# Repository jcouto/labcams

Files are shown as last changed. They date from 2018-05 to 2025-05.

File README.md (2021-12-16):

                                             MMM
                                           MMMMMM
    MMM:               .MMMM             MMMM MMMMMMMM
    MMM:               .MMMM            MMMMM MMMMMMMM      
    MMM:               .MMMM             MMMM  MMMMMM        MM 
    MMM:  :MMMMMMMMM.  .MMMMOMMMMMM       MN     MMM      MMMMM 
    MMM:  :M     MMMM  .MMMMM?+MMMMM    MMMMMMMMMMMMMMM7MMMMMMM  
    MMM:         OMMM  .MMMM    MMMM    MMMMMMMMMMMMMMMMMMMMMMM 
    MMM:  .MMMMMMMMMM  .MMMM    ?MMM    MMMMMMMMMMMMMMMMMMMMMMM 
    MMM:  MMMM  .8MMM  .MMMM    ZMMM    MMMMMMMMMMMMMMMMMMMMMMM 
    MMM:  MMM=...8MMM  .MMMM    MMMM    MMMMMMMMMMMMMMM.MMMMMMM  
    MMM:  MMMMMMMMMMM  .MMMMMMMMMMM                        MMMM 
    MMM:   MMMMM 8MMM  .MMMM:MMMMZ                            M 

         MMMMMMN  =MMMMMMMM     MMMM.MMMM$ .+MMMM      MMMMMMM: 
       MMMMMMMMM  +MMMMMMMMM$   MMMMMMMMMMMMMMMMMM   MMMMMMMMM8 
      MMMM               MMMM   MMMM   MMMM    MMM+  MMM8       
      MMMZ          OMMMMMMMM   MMMM   NMMM    MMM?  MMMMMMM$   
      MMMI        MMMMM  MMMM   MMMM   NMMM    MMM?   ZMMMMMMMM 
      MMMM       7MMM    MMMM   MMMM   NMMM    MMM?        MMMM 
       MMMMD+7MM  MMMN   MMMM   MMMM   NMMM    MMM?  MM$:.7MMMM   
        MMMMMMMM  ZMMMMMOMMMM   MMMM   NMMM    MMM?  MMMMMMMM+  
                          https://bitbucket.org/jpcouto/labcams   

Multicamera control and acquisition.

This aims to facilitate video acquisition and automation of experimens, uses separate processes to record and store data. Interfaces with other computers via UDP or ZeroMQ for automating experiments. Uses hardware and FFMPEG to compress in real-time. 

## Instalation from pip (recommended but not the latest version):

``pip install labcams`` or add the ``--no-deps`` flag to install no dependencies.

Install camera [drivers](./camera_instructions.md):

## Usage:

Open a terminal and type ``labcams -h`` for help.

The first time you run ``labcams`` it will create a folder in the user home directory where the default preference file is stored.

### Command line options:

|       |  command     | description |
|-------|--------------|-------------|
| ``-w``| ``--wait``   | start with software trigger OFF |
| ``-t``| ``--triggered`` |  start with hardware trigger ON |
| ``-c X Y`` | ``--cam-select X Y``     |  start only some cameras ``-c 0 1`` |
| ``-d PATH`` | ``--make-config PATH``  |  create a configuration file |
| | ``--no-server`` | do not start the ZMQ nor the UDP server |

## Configuration files:

Configuration files ensure you always use the same parameters during your experiments.

The configuration files are simple ``json`` files. There are 2 parts to the files.

1. ``cams`` - **camera descriptions** - each camera has a section to store acquisition and recording parameters.

Available camera drivers:

 * `PCO` - install pco.sdk
 * `AVT` - install Vimba SDK and pymba
 * `QImaging` 
 * `pointgrey` - FLIR cameras - install Spinnaker
 * `openCV` - webcams and so on

For calcium or voltage imaging with the PCO (or another) camera use the arduino code in the ``duino`` folder and [instructions](./camera_instructions.md).

Each camera has its own parameters, there are some parameters that are common to all:

* `recorder` - the type of recorder `tiff` `ffmpeg` `opencv` `binary`
 * `haccel` - `nvidia` or `intel` for use with ffmpeg for compression.

**NOTE:** You need to get ffmpeg compiled with `NVENC` from [here](https://developer.nvidia.com/ffmpeg) - precompiled versions are avaliable - `conda install ffmpeg` works. Make sure to have python recognize it in the path (using for example `which ffmpeg` to confirm from git bash)/

**NOTE** To use `intel` acceleration you need to download the [mediaSDK](https://software.intel.com/content/www/us/en/develop/tools/media-sdk.html).

2. **general parameters** to control the remote communication ports and general gui or recording parameters.

 * `recorder_frames_per_file` number of frames per file
 * `recorder_path` the path of the recorder, how to handle substitutions - needs more info.

3. Aditional parameters:

 * 'CamStimTrigger' - controls the arduino camera trigger, see the duino examples folder.

### UDP and ZMQ:

``labcams`` can listen for UDP or ZMQ commands.

To configure use the command ``"server":"udp"`` in the end of the config file.

The port can be configured with ``"server_port":9999``

The UDP commands are:

 * Set the experiment name ``expname=EXPERIMENT_NAME``
 * Software trigger the cameras ``softtrigger=1`` (multiple cameras are not in sync)
 * Hardware trigger mode and save ``trigger=1``
 * Start/stop saving ``manualsave=1``
 * Add a message to the log ``log=MESSAGE``
 * Quit ``quit``

### Supported cameras -  [see instructions here](./camera_instructions.md):

 * PCO cameras (only windows)
 * PointGrey cameras (via PySpin)
 * Basler cameras (via pypylon)
 * Allied Vision Technologies (via pymba - updating to the latest)
 * QImaging cameras via the legacy driver (only windows)
 * Ximea cameras

### Features:

 * Separates viewer, camera control/acquisition and file writer in different processes.
 * Data from camera acquisition process placed on a cue.
 * Display options: background subtraction; histogram equalization; pupil tracking via the [ mptracker ](https://bitbucket.org/jpcouto/mptracker).	
 * Multiple buffers on Allied vision technologies cameras allows high speed data acquisition.
 * Online compression using ffmpeg (supports hardware acceleration)

## Instalation on Ubuntu 20.04

``sudo apt install python3-matplotlib ipython3 python3-opencv python3-pyqt5 python3-tqdm python3-pip python3-pyqtgraph python3-serial python3-zmq python3-natsort python3-pandas emacs git ssh ffmpeg``

``pip3 install labcams`` - this may end up in ``$HOME/.local/bin`` so add the following to the end of the ``.bashrc`` file: ``export PATH=$PATH:$HOME/.local/bin``

## Instalation - from git:

**Note:** On windows get the [ git bash terminal ](https://git-scm.com/downloads). I had issues running from cmd.exe when installed with conda.

1. Get [ anaconda ](https://conda.io/anaconda.html). Add conda to system PATH when asked. Open a terminal (use git bash if on windows) and type ``conda init bash``.
2. Clone the repository: ``git clone git@bitbucket.org:jpcouto/labcams.git``
3. Go into the cloned ``cd labcams`` folder.
4. Install the required packages, use e.g. ``pip install -r requirements.txt`` or conda install... 
5. Install ``labcams`` with ``python setup.py develop``
6. Follow the [camera specific instalation](./camera_instructions.md) and instructions for syncronization. Each camera must have a section in the ``~/labcams/default.json`` file that is created the first time you try to run the software with the command ``labcams`` from the terminal. Use a text editor to add the correct options. There are examples in the examples folder.
7. Install ffmpeg with anaconda: ``conda install -c conda-forge ffmpeg`` 

You can run ``labcams`` from the command terminal. 

**Please drop me a line for feedback and let the world know if you use this.**

Joao Couto - jpcouto@gmail.com

May 2017

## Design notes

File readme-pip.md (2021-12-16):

# labcams

A package for video acquisition and automation of experimens, uses separate processes to record and store data.

## Usage

Open a terminal and type ``labcams -h`` for help.

The first time you run ``labcams`` it will create a folder in the user home directory where the default preference file is stored.

## Configuration files:

Configuration files ensure you always use the same parameters during your experiments.

The configuration files are simple ``json`` files. There are 2 parts to the files.

A section were each camera is specified and a part with general parameters.

Available camera drivers:

* `PCO` - install pco.sdk
* `AVT` - install Vimba SDK and pymba
* `QImaging` 
* `pointgrey` - FLIR cameras - install Spinnaker
* `openCV` - webcams and so on

Each camera has its own parameters, there are some parameters that are common to all:

* `recorder` - the type of recorder `tiff` `ffmpeg` `opencv` `binary`
* `haccel` - `nvidia` or `intel` for use with ffmpeg for compression.
* 'CamStimTrigger' - controls the arduino camera trigger, see the duino examples folder.

## UDP and ZMQ:

``labcams`` can listen for UDP or ZMQ commands.

To configure use the command ``"server":"udp"`` in the end of the config file.

The port can be configured with ``"server_port":9999``

The UDP commands are:

* Set the experiment name - ``expname=EXPERIMENT_NAME``
* Software trigger the cameras (this is software, multiple cameras are not in sync) - ``softtrigger=1``
* Hardware trigger mode and save - ``trigger=1``
* Start/stop saving - ``manualsave=1``
* Add a message to the log - ``log=MESSAGE``
* Quit - ``quit``

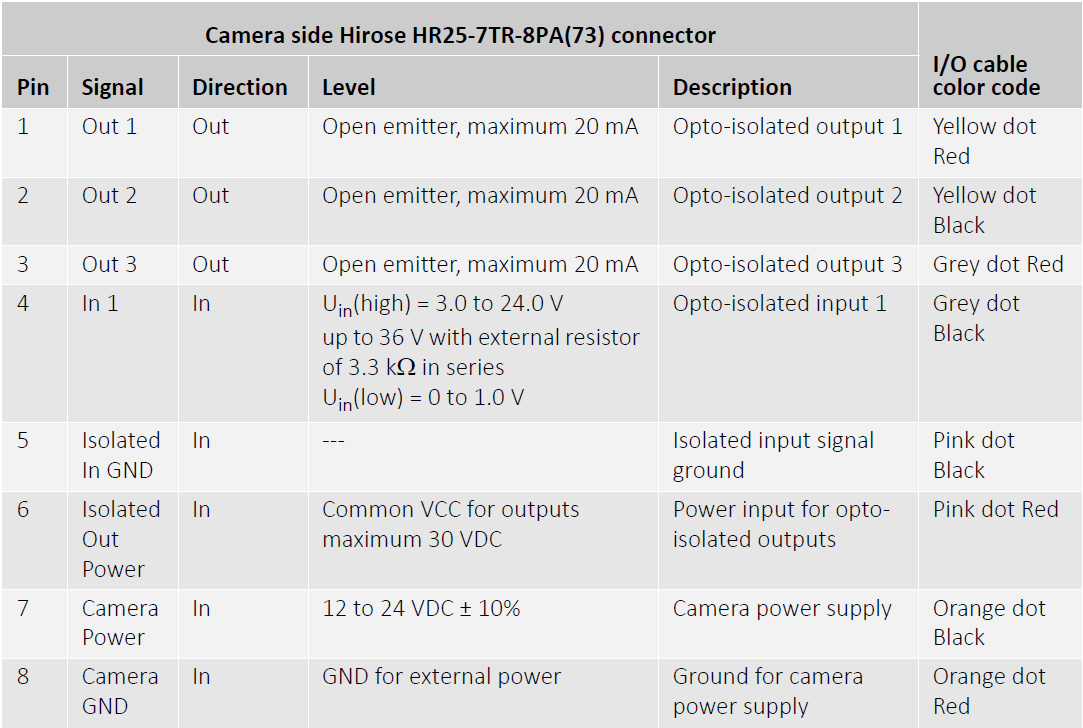
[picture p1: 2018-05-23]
images/mako_conn.png

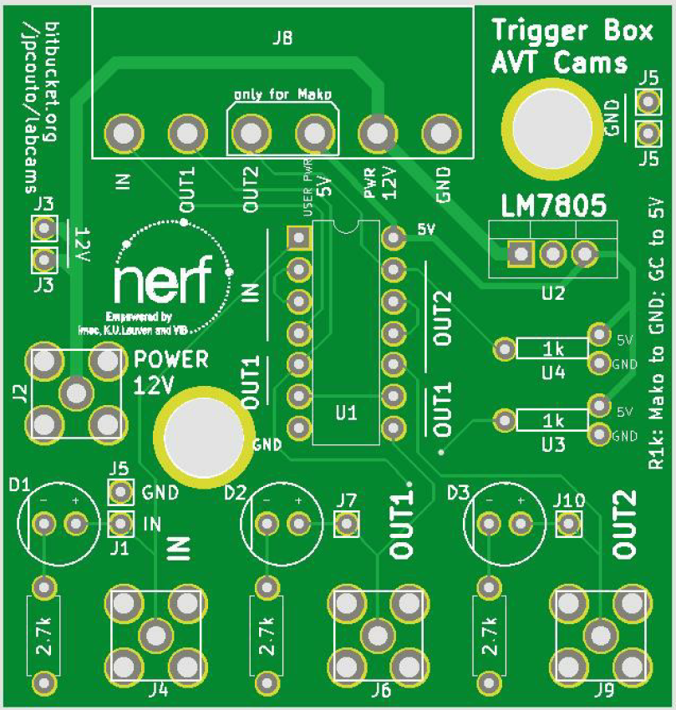
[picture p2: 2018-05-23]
images/trigger_box_avt.png

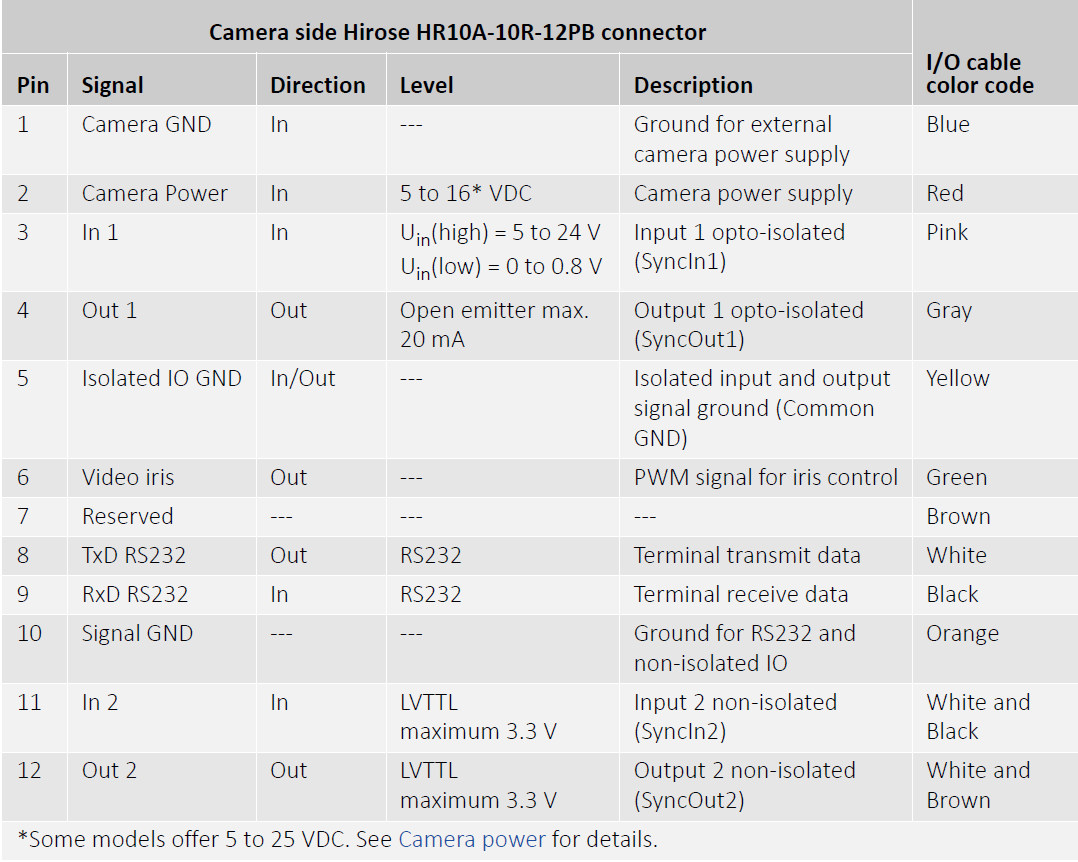
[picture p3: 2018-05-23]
images/gc_conn.png

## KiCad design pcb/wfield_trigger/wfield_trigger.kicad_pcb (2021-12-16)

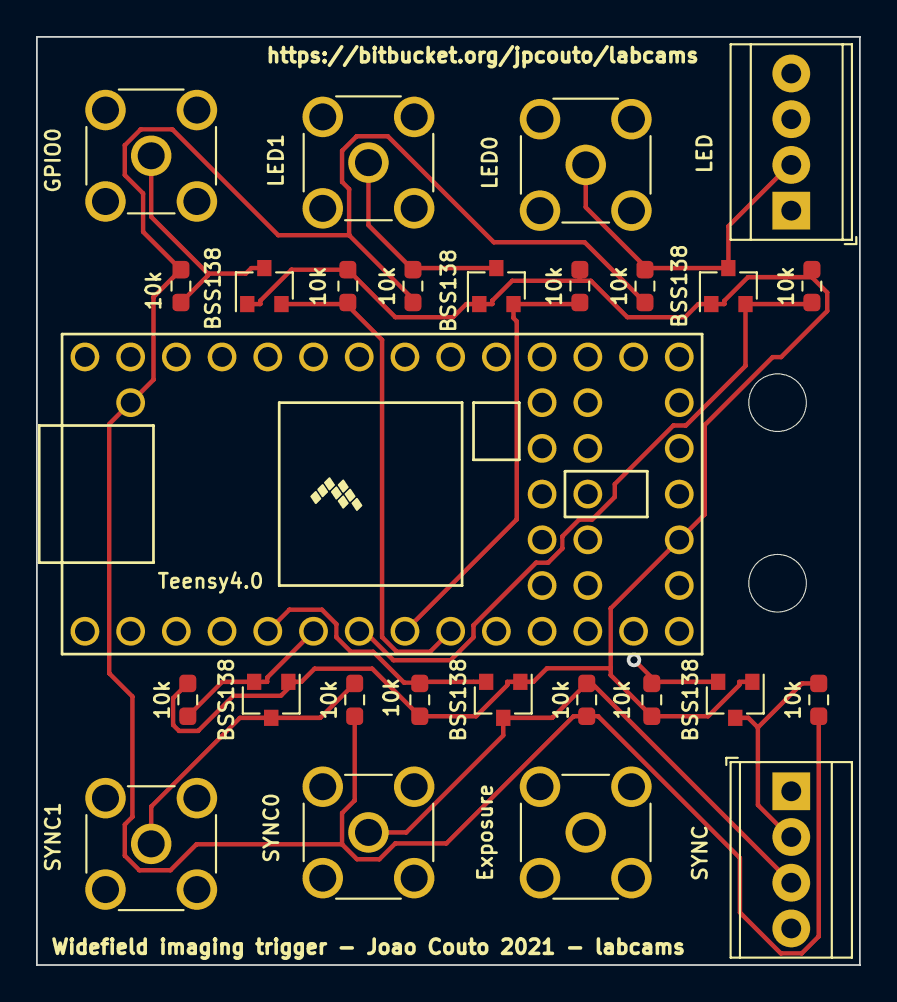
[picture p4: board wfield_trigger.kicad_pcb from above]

Board: 4 copper layers, 45.7 x 51.6 mm, 29 parts (0 on the bottom side), 15 nets.

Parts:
J1: SYNC; TerminalBlock_TE_282834-4_1x04_P2.54mm_Horizontal
J2: LED; TerminalBlock_TE_282834-4_1x04_P2.54mm_Horizontal
J3: LED1; SMA_Molex_73251-2200_Horizontal
J4: Exposure; SMA_Molex_73251-2200_Horizontal
J5: SYNC1; SMA_Molex_73251-2200_Horizontal
J6: SYNC0; SMA_Molex_73251-2200_Horizontal
J7: LED0; SMA_Molex_73251-2200_Horizontal
J8: GPIO0; SMA_Molex_73251-2200_Horizontal
Q1, Q2, Q3, Q4, Q5, Q6: BSS138; SOT-23
R1, R2, R3, R4, R5, R6, R7, R8, R9, R10, R11, R12: 10k; R_0603_1608Metric_Pad0.98x0.95mm_HandSolder
U1: Teensy4.0; Teensy40
mount1, mount2: MountingHole_3.2mm_M3

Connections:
+3V3: Q1.1, Q2.1, Q3.1, Q4.1, Q5.1, Q6.1, R2.1, R4.1, R6.1, R8.1, R10.1, R12.1, U1.16
+5V: R1.2, R3.2, R5.2, R7.2, R9.2, R11.2, U1.34
GND: J1.1, J2.1, J3.2, J4.2, J5.2, J6.2, J7.2, J8.2, U1.1, U1.17, U1.32
cam_trigger: Q1.2, R2.2, U1.4
cam_trigger_out: J1.2, J4.1, Q1.3, R1.1
gpio0: Q6.2, R12.2, U1.9
gpio0_out: J2.4, J8.1, Q6.3, R11.1
led0: Q4.2, R8.2, U1.7
led0_out: J2.2, J7.1, Q4.3, R7.1
led1: Q5.2, R10.2, U1.8
led1_out: J2.3, J3.1, Q5.3, R9.1
sync0: Q2.2, R4.2, U1.5
sync0_out: J1.3, J6.1, Q2.3, R3.1
sync1: Q3.2, R6.2, U1.6
sync1_out: J1.4, J5.1, Q3.3, R5.1

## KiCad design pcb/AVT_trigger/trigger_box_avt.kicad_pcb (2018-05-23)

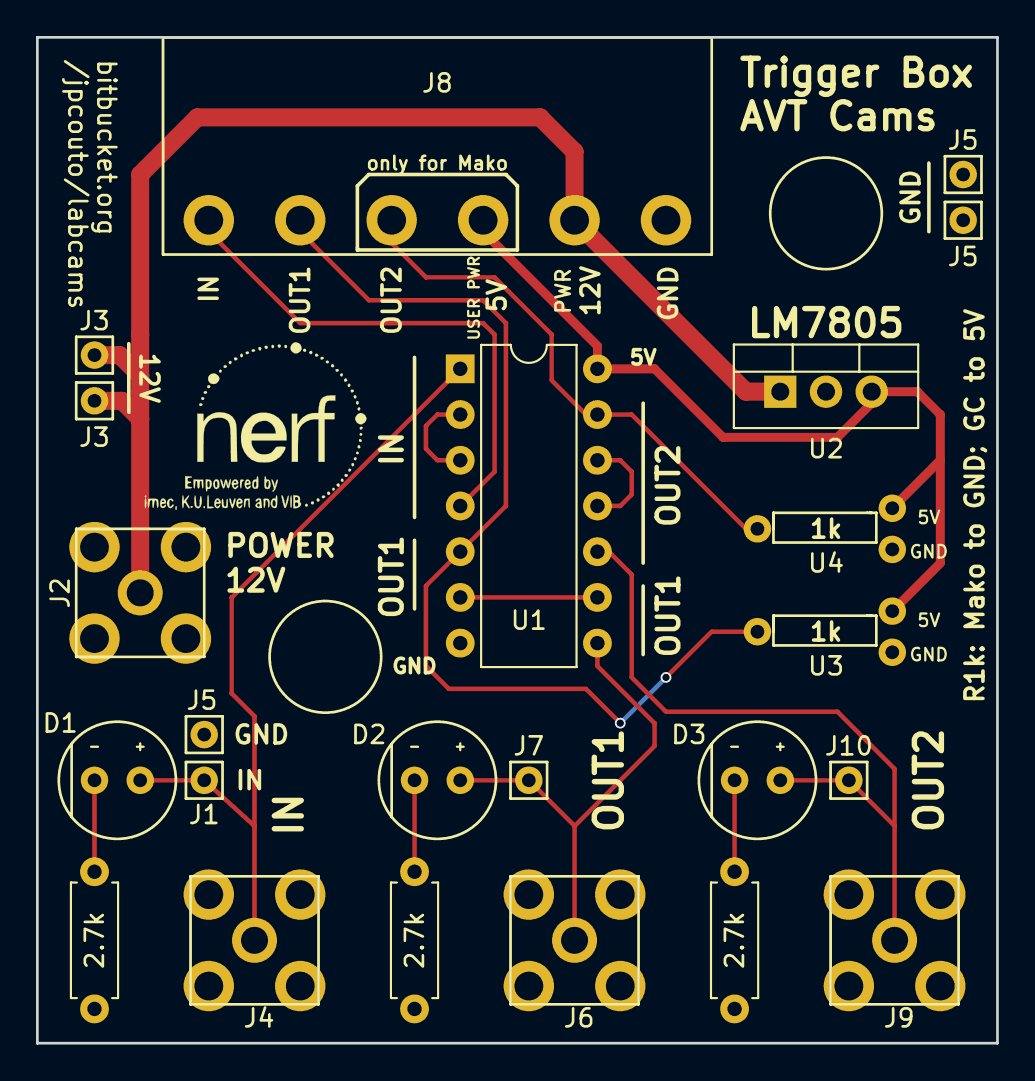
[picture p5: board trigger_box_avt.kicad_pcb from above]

Board: 2 copper layers, 53.3 x 55.9 mm, 23 parts (0 on the bottom side), 15 nets.

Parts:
2.7k, 2.7k#2, 2.7k#3: R; R_Axial_DIN0207_L6.3mm_D2.5mm_P7.62mm_Horizontal
D1, D2, D3: LED; LED_THT_standard
J1, J3, J3#2, J5, J5#2, J5#3, J7, J10: Conn_01x01; conn_01x01
J2, J4, J6, J9: Conn_Coaxial; SMA_female
J8: Conn_01x06; Conn_1x6
U1: 74hct14; DIP-14_W7.62mm
U2: LM7805_TO220; TO-220-3_Vertical
U3, U4: Resistor_choice; Resistor_THT_choice

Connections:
+5V: J8.4, U1.14, U2.3, U3.2, U4.2
+12V: J2.1, J3.1, J3#2.1, J8.5, U2.1
GND: 2.7k.2, 2.7k#2.2, 2.7k#3.2, J1.1, J2.2, J4.2, J5.1, J5#2.1, J6.2, J8.6, J9.2, U1.7, U2.2, U3.3, U4.3
unnamed: 2.7k.1, D1.1
unnamed: 2.7k#2.1, D2.1
unnamed: 2.7k#3.1, D3.1
unnamed: D1.2, J4.1, J5#3.1, U1.1
unnamed: D2.2, J6.1, J7.1, U1.8
unnamed: D3.2, J9.1, J10.1, U1.10
unnamed: J8.1, U1.4
unnamed: J8.2, U1.5, U3.1
unnamed: J8.3, U1.13, U4.1
unnamed: U1.2, U1.3
unnamed: U1.6, U1.9
unnamed: U1.11, U1.12

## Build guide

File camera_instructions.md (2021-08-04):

## Camera specific instructions

# PCO Edge

### Installing drivers and connecting the camera

This camera only works in windows.

Install the PCO.sdk software; make sure to install the correct adapter for your camera (e.g. CameraLink if you have a frame grabber). Install to one of the locations below.

labcams searches for the drivers in:

 * C:\Program Files (x86)\pco\pco.sdk\bin64\SC2_Cam.dll
 * C:\Program Files (x86)\Digital Camera Toolbox\pco.sdk\bin64\SC2_Cam.dll or
 * C:\Program Files (x86)\PCO Digital Camera Toolbox\pco.sdk\bin64\SC2_Cam.dll

**CRITICAL:** For now the PCO camlink camera needs to be initialized before it can be used. You need to open the camera with Camware before opening with ``labcams``. This needs to be done everytime you restart the computer or change the size of the sensor. Change camera properties with CamWare, these will stay

# Connections for widefield imaging using a teensy for sync and alternate illumination

For fast one photon imaging with the PCO (or another) camera you want to use the camera in **rolling shutter mode**. To do this light needs to be ON only during the exposure time common to all lines. These options need to be set in the camera software.

**NOTE:** If CamWare does not have the settings menu available; go to: File -> Options -> Show Camera Control and set it to "Yes".

You can use a teensy to record sync pulses from behavior or stimulus (e.g. using a photodiode on visual display). There are a couple of examples in the duino folder.

Connect the teensy as follows:
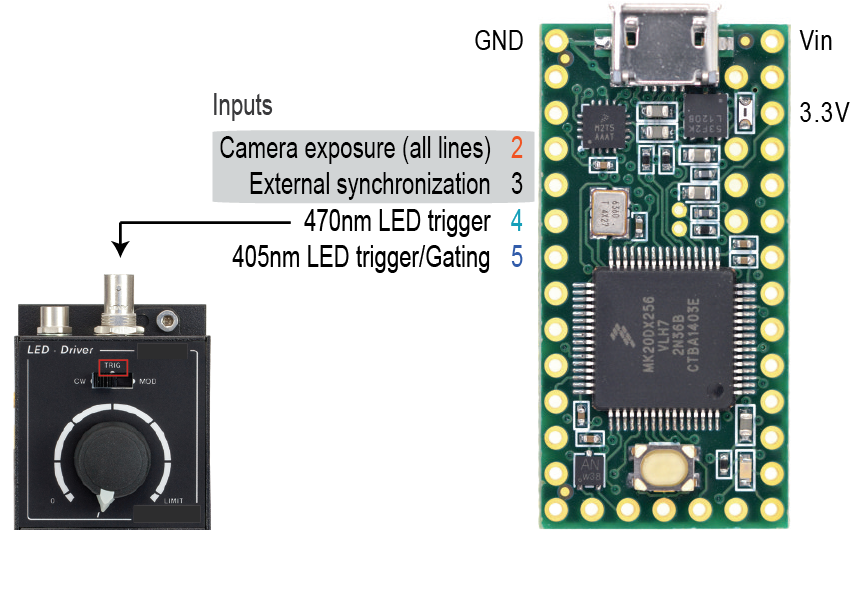
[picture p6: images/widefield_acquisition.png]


The teensy code uses interrupts so that we keep count of even and odd frames.

# Basler cameras

Install the Basler camera drivers "pylon" and the python API.
The python API can be installed with the command ``pip install pypylon`` 

# FLIR cameras

### Installing drivers and connecting the camera

Download SpinView **both the instalation .exe and the python files**. 

**WARNING** Do not do ``pip install pyspin`` the pyspin package in the PyPi project is not the same as the SpinView Python drivers.

* Install the exe
* To install for python you need to download the correct  version for your python instalation (from the FLIR SpinView website).
* Extract the zip and run ``pip install spinnaker_python-2.0.0.147-cp38-cp38-win_amd64.whl`` from the extracted folder (assuming you are using python 3.8).

### Connections for syncronization

To record in sync with behavior you need to connect a **sync TTL** (this from behavior or stimulation hardware) to the pins of the camera. 

On the Chamaeleon 3 USB you can use the Purple wire (GPIO 2). The GPIO states are recorded to the log file and you can use those to sync. 

Make sure the sync pulse is longer than the duration of an individual frame otherwise the camera might miss it.  

# Allied Vision Technologies cameras (AVT):

### Installing drivers and connecting cameras:

* Vimba drivers
* Pymba
* Jumbo packets
* Cable connections and diagram 
     general (camera, computer,ethernet,triggering box)
Connect the Ethernet cable to your computer.
Typically, Vimba Viewer recognizes the camera, but you can not record.
If this is the case then you have to change your IP address. 
On Windows: Control Panel -> Network & Internet -> Network connections -> right-click Ethernet -> Properties -> Networking: Select IPv4 -> Properties -> Use the following IP address. Then change it to a value close to the one of the camera (accessible in the Vimba Viewer in the �information� tab on the right). In my case I used 168.254.100.0 for the IP address and 255.255.0.0 for the subnet mask.

##### Connections for the GC camera

We are only using the first 5 pins of the camera.

Camera Signal|Wire Color|Trigger box pin
------------ | -------- | --------------
Camera GND|Blue|GND
Camera Power|Red|PWR 12V
In 1| Pink|IN
Out 1|Gray|OUT1
Isolated IO GND|Yellow|GND

GC Hirose HR10A-10R-12PB connector [Complete table](images/gc_conn.png)
 
##### Connections for the Mako

We are using 7 pins of the camera (all except Out3).

Camera Signal|Wire Color|Trigger box pin
------------ | -------- | --------
Out 1|Yellow dot Red|OUT1
Out 2|Yellow dot Black|OUT2
In 1|Grey dot Black|IN
Isolated In GND|Pink dot Black|GND
Isolated Out Power|Pink dot Red|USER PWR 5V
Camera power|Orange dot Black|PWR 12V
Camera GND|Orange dot Red|GND

Mako Hirose HR25-7TR-8PA(73) connector [Complete table](images/mako_conn.png)

### Triggering printed circuit board
The triggering printed circuit board has been tested with AVT cameras. It can be used to
   - power cameras;
   - access the camera output
   - trigger cameras with TTL signals.

It uses a schmitt trigger for normalizing the outputs

#### Circuit diagram

Power is on the left, camera interface on top and Arduino interface on bottom.
Only 2 outputs are used: the GC can only use 1, and while the Mako can use up to 3, there is no likely scenario where 3 outputs are needed.

The two main components of the board are a Hex Inverter with Schmitt trigger (74HCT14) and a voltage regulator (LM7805).


The schematics and PCB were done in KiCad ([Design files](pcb/)) by Adrian Philippon in the Bonin Lab at NERF.

* There is an indicator LED for each trigger connection.
* The 1k resistors (U3 and U4) are the pull up/down resistors for the camera outputs, and can be connected either to 5V (for the AVT GC) or GND (for the AVT Mako).
* Some pins are repeated (e.g. 12V, GND) to allow juxtaposition of several trigger boxes. This allows several boards to share the same power supply and trigger source.
* The two holes are M6.

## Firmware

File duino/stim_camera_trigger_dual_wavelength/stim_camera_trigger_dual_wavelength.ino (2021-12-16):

const byte PIN_CAM_EXPOSURE = 2;
const byte PIN_SYNC0 = 3;
const byte PIN_SYNC1 = 4;
const byte PIN_LED0_TRIGGER = 5;
const byte PIN_LED1_TRIGGER = 6;
const byte PIN_GPIO = 7;
#define GPIO_MIMIC_EXPOSURE
volatile long current_time = 0;
volatile long start_time = 0;
volatile long last_pulse_count = 0;
volatile long last_rise = -1;
volatile byte last_led = 0;

//sync counts
volatile long last_sync_rise = -1;
volatile long sync_count = 0;
volatile long sync_frame_count = 0;

volatile long pulse_count = 0; // number of pulses to trigger
volatile byte mode = 3;       // mode 0 : trigger the camera only
                              // mode 1 : LED0
                              // mode 2 : LED1
                              // mode 3 : LEDs alternate
volatile byte armed = 0;      // whether the triggers are armed  

// Serial communication
#define STX '@'
#define ETX '\n'
#define SEP "_"
#define CAP "NCHANNELS_2_MODES_470nm:405nm:both" // capabilities for interfacing with labcams
#define QUERY_NCHANNELS 'C'
#define QUERY_CAP 'Q'
#define START_LEDS 'N'
#define STOP_LEDS 'S'
#define FRAME 'F' // signal the frame time
#define SYNC 'T' // signal the sync time

//#define SET_PARAMETERS 'P' // placeholder
#define SET_MODE 'M' // set the width and the delay

// Serial communication "receive"
# define MSGSIZE 64
char msg[MSGSIZE];
int cnt = 0;

// interrupt to handle flipping the LEDS
void camera_triggered() {
  if (digitalReadFast(PIN_CAM_EXPOSURE) == LOW) {
        digitalWriteFast(PIN_LED0_TRIGGER, LOW);
      digitalWriteFast(PIN_LED1_TRIGGER, LOW);  
      #ifdef GPIO_MIMIC_EXPOSURE
        digitalWriteFast(PIN_GPIO, LOW);
       #endif
  } else {
    
  if (armed) {
    pulse_count++;
    // set the time of the next pulse
    byte pin;
    switch (mode) {
      case 1:
          pin = PIN_LED0_TRIGGER;
          break;
      case 2:
          pin = PIN_LED1_TRIGGER;
          break;
      case 3:
      {
        int tmp = pulse_count % 2;
        if (tmp == 0)
          pin = PIN_LED1_TRIGGER;
        else
          pin = PIN_LED0_TRIGGER;
      }
        break;
      default:
          pin = PIN_LED0_TRIGGER;
    }
    digitalWriteFast(pin, HIGH);
    #ifdef GPIO_MIMIC_EXPOSURE
      digitalWriteFast(PIN_GPIO, HIGH);
    #endif
    last_rise = millis() - start_time;
    last_led = pin;
    last_pulse_count = pulse_count;    
  }
}
}

void sync_received() {
  if (digitalReadFast(PIN_SYNC0) == HIGH)
    sync_count++;
  sync_frame_count = pulse_count;
  last_sync_rise = millis() - start_time;
  }


void setup() {
  pinMode(PIN_LED0_TRIGGER, OUTPUT);
  pinMode(PIN_LED1_TRIGGER, OUTPUT);
  pinMode(PIN_GPIO, OUTPUT);
  pinMode(PIN_SYNC0, INPUT);
  pinMode(PIN_SYNC1, INPUT);
  pinMode(PIN_CAM_EXPOSURE, INPUT);

  digitalWriteFast(PIN_LED0_TRIGGER, LOW);
  digitalWriteFast(PIN_LED1_TRIGGER, LOW);

  Serial.begin(2000000);
  attachInterrupt(digitalPinToInterrupt(PIN_CAM_EXPOSURE), camera_triggered, CHANGE);
  attachInterrupt(digitalPinToInterrupt(PIN_SYNC0), sync_received, CHANGE);
  start_time = millis(); // use micros if more precision needed
}

void loop() {
  current_time = millis() - start_time;
  if ((last_rise > 0) & (abs(current_time - last_rise)> 10)) { // this is limited to 10ms
    Serial.print(STX);
    Serial.print(FRAME);
    Serial.print(SEP);
    Serial.print(last_led);
    Serial.print(SEP);
    Serial.print(last_pulse_count);
    Serial.print(SEP);
    Serial.print(last_rise);
    Serial.print(ETX);
    last_rise = -1;
  }
  if (last_sync_rise > 0){ // this is limited to 10ms
    Serial.print(STX);
    Serial.print(SYNC);
    Serial.print(SEP);
    Serial.print(sync_frame_count);
    Serial.print(SEP);
    Serial.print(sync_count);
    Serial.print(SEP);
    Serial.print(last_sync_rise);
    Serial.print(ETX);
    last_sync_rise = -1;
}
}
void serialEvent()
{
  while (Serial.available()) {
    char ch = Serial.read();
    char* token;
    if (ch == STX || cnt > 0) {
      msg[cnt] = ch;
      cnt++;
      if (ch == ETX) {
        cnt = 0;
        String reply = String(STX);
        switch (msg[1]) {
          case START_LEDS:
            // @N
            last_sync_rise = -1;
            last_rise = -1;
            start_time = millis();
            pulse_count = 0;
            sync_frame_count = 0;
            sync_count = 0;
	    last_pulse_count = 0;
            armed = 1;
            
            reply += START_LEDS;
            Serial.print(reply);
            Serial.print(SEP);
            Serial.print(current_time);
            Serial.print(ETX);
            break;
        case STOP_LEDS:
            // @S
            armed = 0;
            reply += STOP_LEDS;
            Serial.print(reply);
            Serial.print(SEP);
            Serial.print(current_time);
            Serial.print(ETX);
            break;
        case QUERY_CAP:
            // @Q
            reply += QUERY_CAP;
            Serial.print(reply);
            Serial.print(SEP);
            Serial.print(CAP);
            Serial.print(ETX);
            break;
        case SET_MODE:
            // @M
            token = strtok(msg, SEP);
            token = strtok(NULL, SEP);
            mode = atoi(token);
            reply += SET_MODE;
            Serial.print(reply);
            Serial.print(SEP);
            Serial.print(mode);
            Serial.print(ETX);
            break;
          case QUERY_NCHANNELS:
            // @C
            reply += QUERY_NCHANNELS;
            Serial.print(reply);
            Serial.print(SEP);
            if (mode < 3) 
              Serial.print(1);
            else              
              Serial.print(2);
            Serial.print(ETX);
            break;          
          default:
            reply += "E";
            reply += 1;
            reply += ETX;
            Serial.print(reply);
            break;
        }
      }
    }
  }
  Serial.flush();
}

          /*case SET_PARAMETERS:
            setParameters(msg);
            reply += SET_PARAMETERS;
            Serial.print(reply);
            Serial.print(SEP);
            Serial.print(pulse_width);
            Serial.print(SEP);
            Serial.print(pulse_delay);
            Serial.print(ETX);
            break;*/

/*void setParameters(char* msg)
{
  // parameters are formated like: WIDTH_MARGIN
  char* token;
  // Parse string using a (destructive method) 
  token = strtok(msg, SEP);
  token = strtok(NULL, SEP);
  pulse_width = atoi(token);
  token = strtok(NULL, SEP); 
  pulse_delay = atoi(token);
  // need to acknowledge that this was set
}
*/

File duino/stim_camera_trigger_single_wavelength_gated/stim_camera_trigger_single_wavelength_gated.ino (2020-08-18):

const byte PIN_CAM_EXPOSURE = 2;
const byte PIN_SYNC = 3;
const byte PIN_LED0_TRIGGER = 4;
const byte PIN_GATE = 5;


volatile long current_time = 0;
volatile long start_time = 0;
volatile long last_pulse_count = 0;
volatile long last_rise = -1;
volatile byte last_led = 0;

//sync counts
volatile long last_sync_rise = -1;
volatile long sync_count = 0;
volatile long sync_frame_count = 0;

//gate counts
volatile long last_gate_rise = -1;
volatile long gate_count = 0;
volatile long gate_frame_count = 0;

volatile long pulse_count = 0; // number of pulses to trigger
volatile byte armed = 1;      // whether the triggers are armed  
volatile byte gating = 1;      // whether the gate is up

// Serial communication
#define STX '@'
#define ETX '\n'
#define SEP "_"
#define CAP "NCHANNELS_1" // capabilities for interfacing with labcams

#define QUERY_CAP 'Q'
#define START_LEDS 'N'
#define STOP_LEDS 'S'
#define FRAME 'F' // signal the frame time
#define SYNC 'T' // signal the sync time
#define GATE 'U' // signal the sync time

//#define SET_PARAMETERS 'P' // placeholder
#define SET_MODE 'M' // set the width and the delay

// Serial communication "receive"
# define MSGSIZE 64
char msg[MSGSIZE];
int cnt = 0;

// interrupt to handle flipping the LEDS
void camera_triggered() {
  if (digitalReadFast(PIN_CAM_EXPOSURE) == LOW) {
        digitalWriteFast(PIN_LED0_TRIGGER, LOW);
  } else {    
  if (armed) {
      pulse_count++;
      if (gating) {
        digitalWriteFast(PIN_LED0_TRIGGER, HIGH);
        last_rise = micros() - start_time;
        last_led = PIN_LED0_TRIGGER;
        last_pulse_count = pulse_count;  
      }
    }  
}
}

void sync_received() {
  if (digitalReadFast(PIN_SYNC) == HIGH)
    sync_count++;
  sync_frame_count = pulse_count;
  last_sync_rise = micros() - start_time;
  }

void gate_received() {
  if (digitalReadFast(PIN_GATE) == HIGH) {
    gate_count++;
    gating = 0;
  }
  else {
    gating = 1;
  }
  gate_frame_count = pulse_count;
  last_gate_rise = micros() - start_time;
  }

void setup() {
  pinMode(PIN_LED0_TRIGGER, OUTPUT);
  pinMode(PIN_SYNC, INPUT);
  pinMode(PIN_GATE, INPUT);

  pinMode(PIN_CAM_EXPOSURE, INPUT);

  digitalWriteFast(PIN_LED0_TRIGGER, LOW);
  
  Serial.begin(2000000);
  attachInterrupt(digitalPinToInterrupt(PIN_CAM_EXPOSURE), camera_triggered, CHANGE);
  attachInterrupt(digitalPinToInterrupt(PIN_SYNC), sync_received, CHANGE);
  attachInterrupt(digitalPinToInterrupt(PIN_GATE), gate_received, CHANGE);
  start_time = micros(); // use micros if more precision needed
}

void loop() {
  current_time = micros() - start_time;
  if ((last_rise > 0) & (abs(current_time - last_rise)> 9000)) { // this is limited to 10ms
    Serial.print(STX);
    Serial.print(FRAME);
    Serial.print(SEP);
    Serial.print(last_led);
    Serial.print(SEP);
    Serial.print(last_pulse_count);
    Serial.print(SEP);
    Serial.print(last_rise/1000.);
    Serial.print(ETX);
    last_rise = -1;
    
  }
  if (last_sync_rise > 0){ 
    Serial.print(STX);
    Serial.print(SYNC);
    Serial.print(SEP);
    Serial.print(sync_frame_count);
    Serial.print(SEP);
    Serial.print(sync_count);
    Serial.print(SEP);
    Serial.print(last_sync_rise/1000.);
    Serial.print(ETX);
    last_sync_rise = -1;
}
if (last_gate_rise > 0){ 
    Serial.print(STX);
    Serial.print(GATE);
    Serial.print(SEP);
    Serial.print(gate_frame_count);
    Serial.print(SEP);
    Serial.print(gate_count);
    Serial.print(SEP);
    Serial.print(last_gate_rise/1000.);
    Serial.print(ETX);
    last_gate_rise = -1;
}
}
void serialEvent()
{
  while (Serial.available()) {
    char ch = Serial.read();
    //char* token;
    if (ch == STX || cnt > 0) {
      msg[cnt] = ch;
      cnt++;
      if (ch == ETX) {
        cnt = 0;
        String reply = String(STX);
        switch (msg[1]) {
          case START_LEDS:
            // @N
            pulse_count = 0;
            start_time = micros();
            sync_count = 0;
            pulse_count = 0;
            sync_frame_count = 0;

            last_pulse_count = 0;

            last_sync_rise = -1;
            last_rise = -1;
            armed = 1;
            
            reply += START_LEDS;
            Serial.print(reply);
            Serial.print(SEP);
            Serial.print(current_time/1000.);
            Serial.print(ETX);
            break;
        case STOP_LEDS:
            // @S
            armed = 0;
            reply += STOP_LEDS;
            Serial.print(reply);
            Serial.print(SEP);
            Serial.print(current_time/1000.);
            Serial.print(ETX);
            break;
        case QUERY_CAP:
            // @Q
            reply += QUERY_CAP;
            Serial.print(reply);
            Serial.print(SEP);
            Serial.print(CAP);
            Serial.print(ETX);
            break;
          default:
            reply += "E";
            reply += 1;
            reply += ETX;
            Serial.print(reply);
            break;
        }
      }
    }
  }
  Serial.flush();
}

          /*case SET_PARAMETERS:
            setParameters(msg);
            reply += SET_PARAMETERS;
            Serial.print(reply);
            Serial.print(SEP);
            Serial.print(pulse_width);
            Serial.print(SEP);
            Serial.print(pulse_delay);
            Serial.print(ETX);
            break;*/

/*void setParameters(char* msg)
{
  // parameters are formated like: WIDTH_MARGIN
  char* token;
  // Parse string using a (destructive method) 
  token = strtok(msg, SEP);
  token = strtok(NULL, SEP);
  pulse_width = atoi(token);
  token = strtok(NULL, SEP); 
  pulse_delay = atoi(token);
  // need to acknowledge that this was set
}
*/

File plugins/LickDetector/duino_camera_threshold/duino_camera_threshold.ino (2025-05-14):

const byte PIN0 = 1;
const byte PIN1 = 2;
//#define USE_CAPACITIVE
#define LICK0 22
#define LICK1 23
float lick0_value = 0.0;
float lick1_value = 0.0;
float lick0_lpass = 0.0;
float lick1_lpass = 0.0;


float lick0_threshold = 15;
float lick1_threshold = 15;
float threshold_offset = 7;
constexpr float k = 0.1; //0.2
constexpr float klpass = 0.9; //0.999

short lickon0 = 0;
short lickon1 = 0;

#define LISTEN_MSG

void setup() {
  // put youZr setup code here, to run once:
  pinMode(PIN0, OUTPUT);
  pinMode(PIN1, OUTPUT);
  digitalWriteFast(PIN0, LOW);
  digitalWriteFast(PIN1, LOW);
  Serial.begin(2000000);
  #ifdef USE_CAPACITIVE
  pinMode(LICK0, OUTPUT);
  pinMode(LICK1, OUTPUT);
  digitalWriteFast(LICK0, LOW);
  digitalWriteFast(LICK1, LOW);
  #endif
}

void loop() {
  #ifdef USE_CAPACITIVE
   float l0 = touchRead(LICK0);
   float l1 = touchRead(LICK1);

//    Serial.print(',');
   if (l0 < 60000.) // this to prevent some strange behaviour on movement
        lick0_value = (k * l0 + (1 - k) * lick0_value); //k * l0 + (1 - k) * lick0_value;
   lick0_lpass = lick0_lpass*klpass + (1-klpass)*lick0_value;
   if (l1 < 60000.) // this to prevent some strange behaviour on movement
        lick1_value =  (k * l1 + (1 - k) * lick1_value); //k * l0 + (1 - k) * lick0_value;
   lick1_lpass = lick1_lpass*klpass + (1-klpass)*lick1_value;
   
   if (((lick0_value - lick0_lpass) >= lick0_threshold) and (lickon0 == 0)) {
     lickon0 = 1;
     digitalWriteFast(PIN0,HIGH);
   }
   else if (((lick0_value - lick0_lpass) < (lick0_threshold-threshold_offset)) and (lickon0 == 1)) {
      lickon0 = 0;
      digitalWriteFast(PIN0,LOW);
   }
   if (((lick1_value - lick1_lpass) >= lick1_threshold) and (lickon1 == 0)) {
     lickon1 = 1;
     digitalWriteFast(PIN1,HIGH);
   }
   else if (((lick1_value - lick1_lpass) < (lick1_threshold-threshold_offset)) and (lickon1 == 1)) {
      lickon1 = 0;
      digitalWriteFast(PIN1,LOW);
   }

    Serial.print((lick0_value - lick0_lpass));
    Serial.print(',');
    Serial.print((lick1_value  - lick1_lpass));
    Serial.print(',');
    if (lickon0 == 1) Serial.print(45); else Serial.print(30);
    Serial.print(','); 
    if (lickon1 == 1) Serial.println(46); else Serial.println(31); 

   #endif
}


#define UP_MSG 'U'
#define DOWN_MSG 'D'
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

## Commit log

2017-04-02 Camera Array works for frames of uint8. GUI displays data.
2017-04-18 Exposure is set based on frame rate
2017-09-27 Camera triggering for Qimaging.
2018-05-03 Added preferences to json files. Files are closed when recorder is reset. Log file for each camera. Never repeat frames (check id before queueing).
2018-05-04 Changed arg to make config. Number of background frames.
2018-05-05 Use all cameras in the absense of a -c option in the labcams gui.
2018-05-06 Parse camera log function. Function to find files. Preference file on the home dir (preparing to get preferebces frin there). Function to merge camtimes with the pyvstim log.
2018-05-23 Cameras wait to be triggered (with the cameraReady event). Sleep 2 seconds before triggering to ensure sync.
2018-05-23 Updated readme and started skeleton for camera instructions.
2018-05-23 +Design files
    [trigger_box_avt.kicad_pcb, trigger_box_avt.sch]
2018-10-16 Can pass TriggerSelector but switches to FrameStart.
2018-10-16 Manual save does not close cameras. Last buffer cleanup has reversed order so that the last frames of AVT cams are not flipped. Moved the Take screnshot function to inside the camera menu. Remote tri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
2018-10-22 Sorted frame ids on buffer read (AVTcams).
2018-10-30 Can connect to AVT cameras based on partnumber
2019-01-24 Added opencv camera.
2019-01-26 Vertically stack cameras. Eye parameter widget moved from parent.
2019-01-29 Moved widgets from gui.py. Messages with display instead of print. Can select eye tracker area when using the mouse on the main window.
2019-02-13 Trim number of reference frames for baseline in binLaps
2019-02-14 cv threads set in writer for use with mptracker.
2019-02-19 Can specify cameras based on device_id. Example configuration files.
2019-02-21 Triggered prints names.
2019-05-30 Replaced prints with display. Removed deprecated PyQt image scene code.
2019-06-02 Slider on context menu to control n subtracted frames.
2019-10-04 Warning for unknown camera driver.
2019-10-10 Skeleton to control camera parameters from queue
2019-10-12 Draft of control camera parameters during run.
2019-10-22 Replaced asssertion with warning in cameralog-pyvstim parser
2019-10-23 Print campulses and num frames.
2019-10-23 Space before number of frames on no save text.
2019-10-23 Ximea camera support skeleton.
2019-10-25 Ximea triggered on input1 and out1 sends pulse when frame acquired (computer controlled quick fix).
2019-10-25 Ximea disable LED lights.
2019-10-31 Interpolate on first and last frame when sync is messed up.
2020-01-19 Use camera id for point grey cameras
2020-01-20 Added roi selection to PointGrey cameras. [Warning: labcams expects valid rois.]
2020-02-05 Pass frame rate to writer when ffmpeg or opencv. Use intel hardware on ffmpeg. Close writer from the cam queue.
2020-02-13 binning and exposure control for pointgrey cameras.
2020-02-25 Reset sensor image size before setting.
2020-03-07 test pco python sdk. made ctypes implementation work with latest pco sdk (camera handle and so on).
2020-03-07 pco updated to get frameid from frame first bytes.
2020-03-08 Arduino code for driving LEDs with camera exposure pulse. PCO updated to stop acquiring on software trigger.
2020-03-09 Camera excitation LED controller for widefield imaging.
2020-03-09 Save LED info to the log when using with PCO.
2020-03-10 nframes is the frame id in avt and point grey cameras
2020-03-12 No trackerToggle on mptracker. Nan mean of the roi. Disable sharpness auto on pointgrey cameras.
2020-04-14 LED control using common exposure TTL.
2020-05-24 Prevent crash when failing to set frame rate on pgcamerage
2020-06-15 BinaryCamWriter for recording on acquisition when the queue is the bottleneck (e.g. PCO at 500Hz).
2020-06-17 Allow multiple messages sent to log. Hardware trigger for linking 2 CM3 cameras
2020-06-26 Start stim teensy in the armed reset state
2020-06-27 PointGrey camera default to no ExposureAuto off, SharpnessAuto off and set line 3 to output if hardware_trigger out_line3
2020-06-28 Corrected LED order so that the first frame is iluminated by LED0.
2020-06-28 Removed legacy ffmpeg. Camera exposure of triggered is timed.
2020-07-01 Can start pco without teensy
2020-07-01 PCO does not need teensy and recent PCO.sdk path added.
2020-07-07 Added way to probe capabilities and modes from the teensy.
2020-07-07 Teensy code for single LED stim.
2020-07-07 PCO takes binning from camera if None. Set combo stim mode to nothing.
2020-07-07 Handle the whole log queue when closing internal recorder thread. Change SaveMethod option to recorder.
2020-07-09 Changed sync log order. Instructions when camera driver fails load.
2020-07-09 Teensy resets sync time before changing the sync_count.
2020-07-14 parseCamLo can read teensy comments.
2020-08-18 PCO test with sync at 500Hz - works. Sync read for SYNC1: from the teensy.
2020-08-18 Example to check sync between PCO and teensy.
2020-08-20 Draft of camera instructions.
2020-08-20 camera_instructions.md edited, images not rendering
2020-09-04 Multiple frames per file in ffmpeg.
2020-09-10 Can use lowecase names in the camera, SaveMethod is still accepted. Readme updated.
2020-09-19 PointGrey go set auto framerate off
2020-11-25 Changed order of cameras so the master is the last if ordered on the file. Delay before triggering master.
2020-11-28 Multiple FLIR cameras working on linux (spawn). Sync between flir cameras improved.
2020-12-03 Channels passed to the recorders. Enter on edit saves filename. Recorders init method sets nchannels and frame_rate. Frame rate defined for all cam drivers.
2020-12-11 GUI for selecting cameras has elements.
2020-12-29 Sleep the triggered camera from FLIR before stopping acquisition.
2021-03-19 Added support for basler cameras.
2021-06-02 Smaller size for teensy box.
2021-09-20 Solved BlackFly S cameras issues while setting frame rate and for synchronizing. Gamma, exposure and gain setting dont crash cameras if oyt of range. Added cam id to some displays.
2021-09-29 Change the frame rate enable before trying to disable auto for chamaeleon cameras.
2021-11-02 Firefly cameras also don t have set auto.
2021-11-05 PCB for widefield triggering.
    [trigger_box_avt.kicad_pcb, trigger_box_avt.sch, wfield_trigger.kicad_pcb, wfield_trigger.sch]
2021-11-14 Set pins for the pcb circuit with teensy 4.0
2021-12-04 Read teensylog even when there are no syncs
2022-02-03 Widget to visualize analog channels. Save analog in int16. Events to nidaq to behave like a camera.
2022-02-07 PointGrey cameras, make sure to read all frames before closing the camera.
2022-04-02 Major changes. Introduced shared memory buffer and now using queue just to pass frame IDs. New class that joins cameras and saving classes for easy operation without the gui. Breaks compatibility wit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
2022-04-05 Recorders using membuffer. OpenCV camera starts,stops and resets frame ids on software trigger.
2022-04-05 Removed acquisition stim trigger from PCO so the excitation control module can be used with any camera.
2022-04-06 Pointgrey tested with new memory buffer. Widgets can control cameras again. Remote working.
2022-04-06 Frame rate in pointgrey called 'frame_rate'. Compatibility with python 3.8.10 on linux for calling datatype.
2022-04-12 Fixed ROI in pointgrey Camera
2022-04-14 NIDAQ working with camera object.
2022-05-20 Pass the save trigger to the camera excitation trigger.
2022-06-02 Can run pointgrey without hardware trigger and frame_rate. Can add plugins updated at every refresh. Seerver does not start by default
2022-07-28 Moved triggering logic from widget to camera. Can pass arbitrary parameters to the recorder dictionary. IBL file updated.
2022-07-29 Don't try to set line 2 and 3 in BlackFly cameras.
2022-08-01 Set buffers on pco to 300; removed error for checking line when cam not acquiring (pointgrey). Auto-update while waiting on cameras to be ready.
2022-08-03 PyPi release server 0.6 with multi-buffer handling on pointgrey cameras and nidaq recording capability.
2022-09-08 Added PVCam to Camera
2022-09-29 Initialize the queues max size. Drop frames if the queue grows forever.
2023-01-09 Log messages get the frameid from the shared object (not lastframeid as previously).
2025-03-27 Can do capacitive touch in the LickDetector plugin to skip the camera.
2025-04-15 Added a warning for the CM3 cameras when not supporting the line.
2025-04-15 Added example to analyze LED sync with FLIR.
2025-04-16 Added FLIR test at 30Hz with PCO and nidaq.
2025-04-28 Added warning when using deprecated frameRate. Added support for asynchronous acquisition with AVT cams.
